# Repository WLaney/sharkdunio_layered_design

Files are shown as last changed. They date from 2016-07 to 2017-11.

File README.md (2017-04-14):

# sharkduino_layered_desgine

This repository contains the Eagle designs and design information for the Sharkduino PCBs. The name sharkduino_layered_desgin is a legacy name referring to the design type used by Sharkduino V1. This repository does however contains all versions of Shakrduino, not just V1. Please see [Sharkduino Versions](#sharkduino-versions) for more information. For the spefic chips and ports on each version please see [Hardware Quick Reference](https://github.com/WLaney/sharkdunio_layered_design/blob/master/hardware_quick_reference.md)

# Sharkduino Versions

This is an explanation of the different sharkduino versions and the directories in this repository that contain them

## Sharkduino V1

Sharkduino V1 uses a layer designs and consists of [layer1](layer1/), [layer2](layer2/), and [layer3](layer3/). The versions of Sharkduino V1 that were assembled corresponded to the release v2 named "Layered boards". Changes have been made to the boards since then in order to improve them, these changes constitute Sharkduino V1.1. No V1.1 boards were ever ordered or assembled. Instead of ordering V1.1 boards a design overhaul took place and we moved to Sharkduino V2. 

## Sharkduino V2

Sharkduino V2 constitutes a design overhaul from V1 with a new board shape and new set of sensors. These designs can be found in the [trapezoid](trapezoid/) directory. The version of Sharkduino V2 that has been assembled corresponds to release [v5](https://github.com/WLaney/sharkdunio_layered_design/releases/tag/v5) "Sharkduion V2". Since the enviromental sensors need to be sepreate from the movement sensors Shakrduino V2 still uses [layer3](layer3/) form the Sharkduino V1 as no changes to that board were nessary.

## Sharkduino V2.1

Sharkduino V2.1 is an identical PCB to V2, but it uses the MMA8451 accelerometer. This is opposed to the MMA8452 used in the V2. This change was made so that the accelerometer would have a FIFO bufer like the gyroscope. The new accelerometer is an expermental change, so the files are on the [MMA8451 branch](https://github.com/WLaney/sharkdunio_layered_design/tree/mma8451). The first functinoal build of this corosponds to release [v7](https://github.com/WLaney/sharkdunio_layered_design/releases/tag/v7). The change on this branch have since been merged into master.

## Sharkduino V2.2

Sharkduino V2.2 is a slight varation on the Sharkduino V2.x desgine. Due to the [issue with the cargining circuity](https://github.com/WLaney/sharkdunio_layered_design/issues/1) the microUSB and lipo charger were removed from the board. This was done in order to have a set of fully functional board ready for summer 2017. 

The LiPo plug was moved to the top of the board in order to streamline the desgine. Additionaly interupt pin2 on the FXAS21002 gyroscope was connected Arduino pin 2. 

Since in the long term we plan to fix the LiPo charging issue, instead of removing the LiPo chargin all together as we have done here, the files for Sharkduino V2.2 are on the [no_chargin branch](https://github.com/WLaney/sharkdunio_layered_design/tree/no_charging) and will never be merged into master. The desgines of the Sharkduino V2.2 that have been order corosponed to release [v8](https://github.com/WLaney/sharkdunio_layered_design/releases/tag/v8).

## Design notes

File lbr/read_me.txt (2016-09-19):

The abracon lbr comes form the following source:
https://github.com/cmonr/Eagle-Libraries/blob/master/Other/abracon.lbr
I have checked it for the abs25 and it looks good. I increased the size of the silk scrren wire width, and added a tdoc layer. The silk sreen crosses the pads, instead of fixing it I'll let the fab house just not print it

the sharkduino lbr is created in full by me

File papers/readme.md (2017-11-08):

# Papers

This directroy contains datasheets for componets on the tag that do not inteact with the Arduino through code. For the reamind data sheets please look in the [Arduino_Animal_Tag repo](https://github.com/sharkduino/Arduino_Animal_Tag/tree/master/papers)

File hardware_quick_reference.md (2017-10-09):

## Sharkduino V1.0
* MMA8452Q Accelerometer
* L3GD20H Gyroscope
* DS3234 RTC
  * Interrupt wired to Arduino pin 2
* Push-Push microSD slot
* JPL male 2 prong connector
* [Broken] MCP7381 LiPo Charge Management Controller
* [Broken] Micro USB female port
* 12mm coin cell slot
### On separate layer 3 board
* TMP102 Temperature Sensor
* MS5803 Temp/Pressure Sensor

## Sharkduino V2.0
*Full Redesign*
* MMA8452Q Accelerometer
  * INT1 pin wired to Arduino pin 3
* FXAS21002 Gyroscope
* DS1339B RTC
  * Interrupt wired to Arduino pin 2
* Push-Pull microSD slot
* JPL male 2 prong connector
* [Broken] MCP7381 LiPo Charge Management Controller
* [Broken] Micro USB female port
* 12mm coin cell slot
### On separate layer 3 board
* TMP102 Temperature Sensor
* MS5803 Temp/Pressure Sensor

## Sharkduino V2.1
*New accelerometer: MMA8451Q*
* MMA8451Q Accelerometer
  * INT1 pin wired to Arduino pin 3
* FXAS21002 Gyroscope
* DS1339B RTC
  * Interrupt wired to Arduino pin 2
* Push-Pull microSD slot
* JPL male 2 prong connector
* [Broken] MCP7381 LiPo Charge Management Controller
* [Broken] Micro USB female port
* 12mm coin cell slot
### On separate layer 3 board
* TMP102 Temperature Sensor
* MS5803 Temp/Pressure Sensor

## Sharkduino V2.2
*Connected FXAS21002 Gyroscope interupt*

*Removed MCP7381 LiPo Charge Management Controller*

*Removed Micro USB female port*
* MMA8451Q Accelerometer
  * INT1 pin wired to Arduino pin 3
* FXAS21002 Gyroscope
  * INT2 pin wired to Arduino pin 2
* DS1339B RTC
  * Interrupt wired to Arduino pin 2
* Push-Pull microSD slot
* JPL male 2 prong connector
* 12mm coin cell slot
### On separate layer 3 board
* TMP102 Temperature Sensor
* MS5803 Temp/Pressure Sensor

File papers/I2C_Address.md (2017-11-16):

# I2C Address

Found using I2C scaner on V2.2B and V2.0A

| device    | i2c address |
| --------- | ----------- |
| DS1339B   | 0x68        |
| FXAS21002 | 0x20        |
| MMA8451   | 0x1D        |

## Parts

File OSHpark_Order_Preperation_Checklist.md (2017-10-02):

# OSHpark Order Preparation Checklist

* Run Ratsnest and confirm no air wires
* Confirm that all desired pours are accounted for
* Estimate grounding paths on the board and determine if extra ground lines or vias are needed
* Check for non optimal traces on board
* Check for right angle traces on data lines
* Run [oshpark-2layer DRC](http://docs.oshpark.com/design-tools/eagle/design-rules-files/)
* Run [SparkFun DRC](https://www.sparkfun.com/tutorials/115)
  * Please note that this DRC will throw errors for tolerance that OSHpark can handle, when in doubt trust the OSH Park DRC
* Run [oshpark-2layer DRC](http://docs.oshpark.com/design-tools/eagle/design-rules-files/) again
* Run ERC
* If multiple trace sizes are used confirm that they are consistent, and that traces have the same width for there full length
* check components on board against the BOM
* Confirm that all components are labeled on silk
* Confirm that all pins are labeled on silk
* If orientation is important confirm that it is correct and clearly labeled on silk
* Confirm that all product and author info is on silk
* Confirm that all writing on silk is correctly spelled
* Confirm that no silk overlaps exposed copper
* Smash all components
* Delete all tNames and bNames (layers 25 and 26 respectively)
* Upload designs to OSHpark
* Confirm that silk looks good, and writing is positioned correctly
* Confirm that traces look as desired

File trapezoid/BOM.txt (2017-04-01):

component/value, size, quanity, digikey part number
--------------------------------------------------------
Arduino Pro Mini 3.3V/8MHz, NA, 1, 1568-1054-ND
MMA8451QT, 16-VFQFN, 1, MMA8451QT-ND
FXAS21002 IC, 24-TFQFN, 1, FXAS21002CQR1CT-ND
DS1339B IC, 8-TSSOP/8-MSOP, 1, DS1339BU+-ND
Abracon LLC ABS25-32.768KHZ-T, 4-SOJ, 1, 535-9166-1-ND
MCP73831 IC, SC-74A/SOT-753, 1, MCP73831T-2ATI/OTCT-ND
Molex 8+2 microSD slot, NA, 1, WM6357CT-ND
Red LED, 0603, 1, 160-1447-1-ND
0.1uF capacitor, 0805, 6, 478-3755-1-ND
1.0uF capacitor, 0805, 1, 311-1365-1-ND
4.7uF capacitor, 0805, 3, 490-3335-1-ND
330 resistor, 0805, 1, 311-330CRCT-ND
2k resistor, 0805, 1, 311-2.00KCRCT-ND
10K resistor, 0805, 4, 311-10.0KCRCT-ND
47k resistor, 0805, 1, 311-47KARCT-ND
USB micro SMD, NA, 1, 609-4053-1-ND
Curved Battery Holder, 12mm, 1, 36-3000CT-ND
JST Male, 2mm, 1, 455-1749-1-ND
Male Header Pins, 0.10", 1, S1011EC-40-ND
BATTERY LITHIUM 3V COIN 12.5MM, BR1225, 1, P183-ND

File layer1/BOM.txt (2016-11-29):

component/value, size, quanity, digikey part number
--------------------------------------------------------
0.1uF capacitor, 0805, 4, 478-3755-1-ND
4.7uF capacitor, 0805, 1, 490-3335-1-ND
10uF capacitor, 0805, 1, 490-4735-1-ND
10K resistor, 0805, 4, 311-10.0KCRCT-ND
MMA8452QT, 16-VFQFN, 1, 	MMA8452QT-ND
L3GD20HTR IC, 16-LGA, 1, 497-13931-1-ND
microSD SMD, NA, 1, Sparkfun: PRT-00127

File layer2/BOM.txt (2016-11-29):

component/value, size, quanity, digikey part number
--------------------------------------------------------
4.7uF capacitor, 0805, 2, 490-3335-1-ND
22pF capacitor, 0402, 1, 399-7774-1-ND
Red LED, 0603, 1, 160-1447-1-ND
10K resistor, 0805, 1, 311-10.0KCRCT-ND
2k resistor, 0805, 1, 311-2.00KCRCT-ND
330 resistor, 0805, 1, 311-330CRCT-ND
DS3234 IC, 20-SOIC, 1, 	DS3234S#T&RCT-ND
MCP73831 IC, SC-74A/SOT-753, 1, MCP73831T-2ATI/OTCT-ND
Curved Battery Holder, 12mm, 1, 36-3000CT-ND
JST Male, 2mm, 1, 455-1749-1-ND
USB micro SMD, NA, 1, 609-4053-1-ND
Header Pins, NA, 1, S1131EC-40-ND

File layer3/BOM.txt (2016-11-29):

component/value, size, quanity, digikey part number
--------------------------------------------------------
10K resistor, 0805, 1, 311-10.0KCRCT-ND
2.2K resistor, 0805, 2, 311-2.20KCRCT-ND
1k resostor, 0805, 1, 311-1.00KCRCT-ND
0.1uF capacitor, 0805, 2, 478-3755-1-ND
TMP102 IC, SOT-563/SOT-666, 1, 296-26834-1-ND
MS5803-14BA IC, NA, 1, 223-1626-5-ND

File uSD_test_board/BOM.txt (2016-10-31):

component/value, size, quanity, digikey part number
--------------------------------------------------------
Molex 8+2 microSD slot, NA, 1, WM6357CT-ND
Amphenol 8+2 microSD slot, NA, 114-00841-68-1-ND
Hirose 8+2 microSD slot, NA, HR1941CT-ND

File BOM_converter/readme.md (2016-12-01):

# BOM Convertor

This is a simple python script that converts the BOM format used in the Sharkduino project into a format that can be directly uploaded into DigiKey's BOM Manager.

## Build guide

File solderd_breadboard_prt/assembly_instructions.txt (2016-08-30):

Soldered Breadboard Assembly Instructions
=====================

(please note that these steps represent what I beilive to be the optimal order of operations. They may not be. Addionaly not all boards were assembled in this way as I expermented with the order)

1) Cut perfreated breadboard to the correct size
2) Solder Headers onto the breadboard
3) Solder wires that run on the top of the board. Start with VCC and GND conections as these are the longest
4) Creat nessary solder briges on the bottom
5) Solder in wires on the bottom
6) Insure that all nessary points are connected
7) Add extra support headers for the uSD, accel, and gyro
8) Solder I2C wires to the arduino
9) Place batt into RTC
10) Solder arduino, uSD holder, and RTC onto the board
11) Solder I2C wire into bread board
12) Solder on accel and gyro

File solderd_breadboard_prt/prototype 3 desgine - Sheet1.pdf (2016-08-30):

V | G | S | SCL | G | | S | S | V | S | H | H | H | H | H | H | H | H | | | 9 | | | | | 2 | G
| | | | | | | | | | DI | | | | | | | | | CD
| | | | | SCL | | | | | D0 | | | | | | | | | D0
| | | | | SDA | | | | CK | | | | | | | | G
| | | | | | | | | | SW | | | ck | | | | | CK | | | | | | | | S | SCL
| | | | | | | | | | V | | | | | | | | | V
| | | | | | | | | | G | | | | | | | | | DI | | 10 | 11 | 12 | 13 | | | V | G | R
| | | | | | | | | | | | | | | | | | | CS

G V S C D DI

S | G | V | V S | G

SS

SCL

SDA

SDA | SCL

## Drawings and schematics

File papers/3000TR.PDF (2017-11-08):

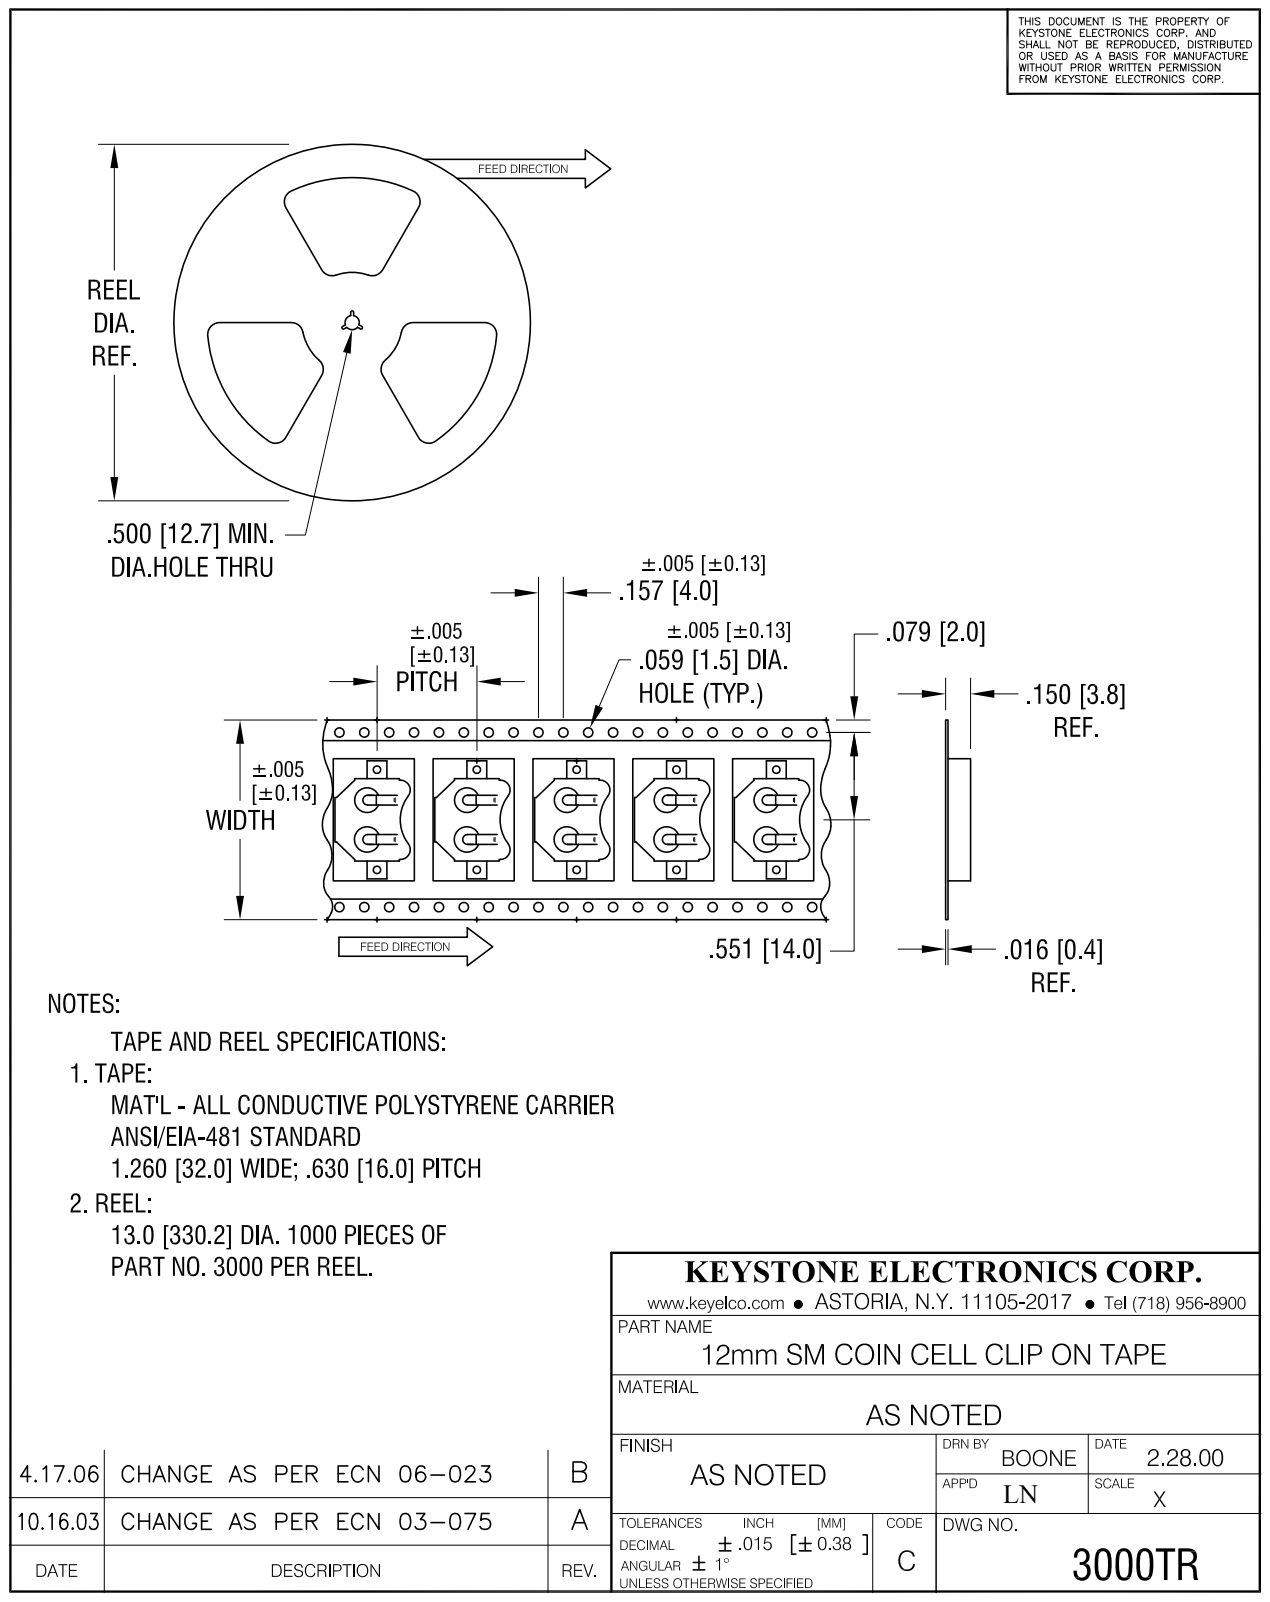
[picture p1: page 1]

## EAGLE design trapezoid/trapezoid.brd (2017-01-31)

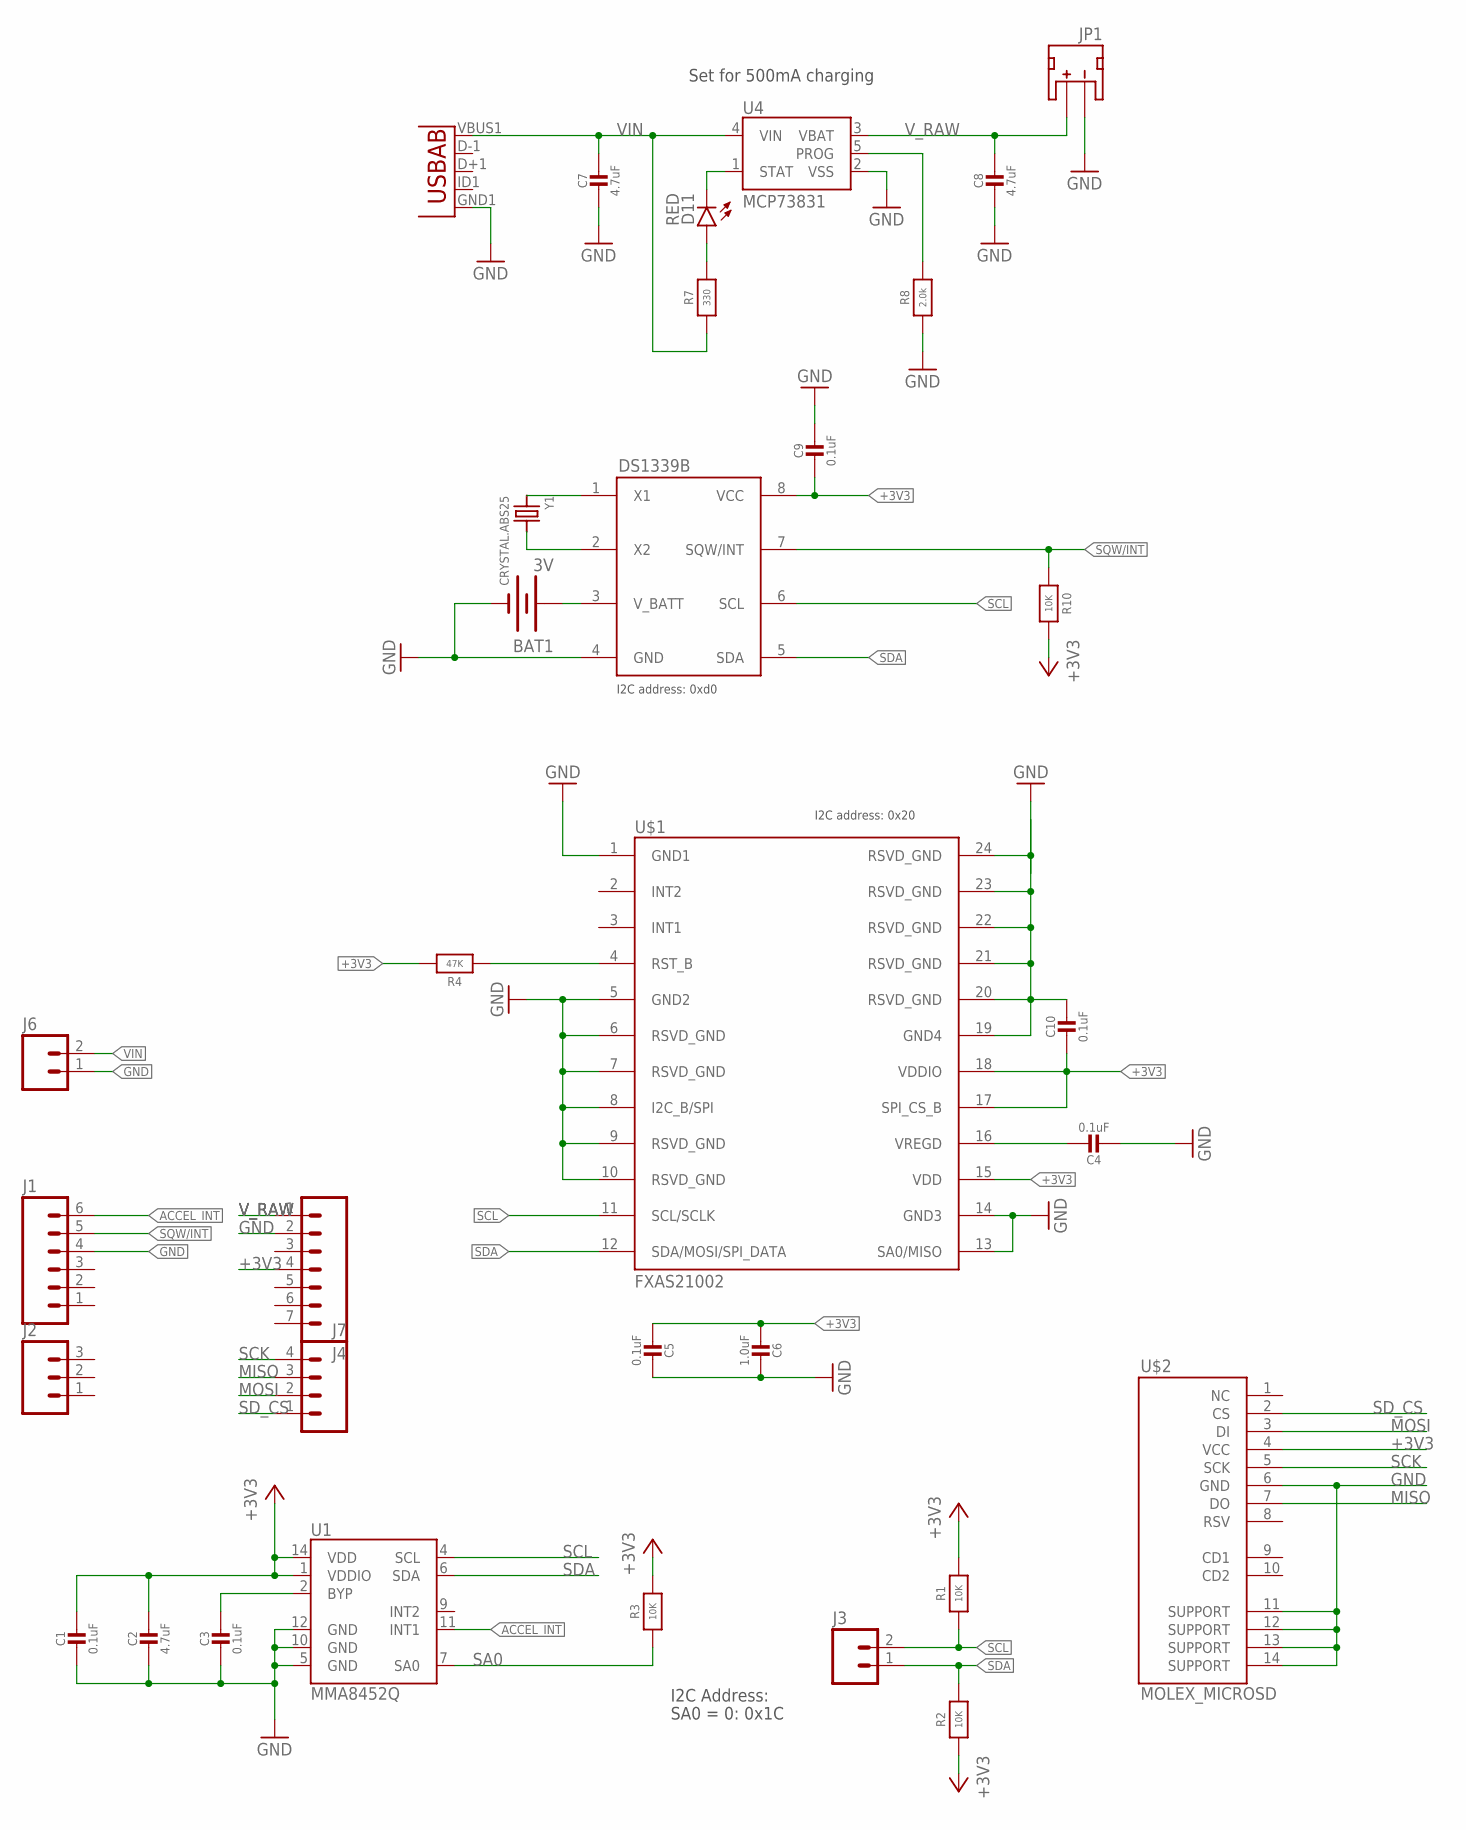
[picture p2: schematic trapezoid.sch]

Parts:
BAT1: 3V; BATTCON_12MM_CURVED
C1, C3, C4, C5, C9, C10: 0.1uF; 0805-NO
C2, C7, C8: 4.7uF; 0805-NO
C6: 1.0uF; 0805-NO
D11: RED; LED-0603
J1: M06SILK_FEMALE_PTH; 1X06
J2: M03PTH; 1X03
J3, J6: M02LOCK; 1X02_LOCK
J4: M07; 1X07
J7: M04PTH; 1X04
JP1: JST; JST-2-SMD@1
JP9: Micro USB; USB-AB-MICRO-SMD_V03
R1, R2, R10: 10K; 0805-NO
R3: 10K; _0805MP
R4: 47K; 0805-NO
R7: 330; _0805MP
R8: 2.0k; _0805MP
U1: MMA8452Q; QFN-16_0.5MM
U4: MCP73831; SOT23-5
U$1: FXAS21002; 24QFN
U$2: MOLEX_MICROSD
U$3: DS1339BDS1339B; 8U-SOP
Y1: CRYSTAL.ABS25; ABS25

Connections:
+3V3: C1.1, C2.1, C5.2, C6.2, C9.2, C10.2, J4.4, R1.2, R2.1, R3.2, R4.2, R10.2, U1.1 (VDDIO), U1.14 (VDD), U$1.15 (VDD), U$1.17 (SPI_CS_B), U$1.18 (VDDIO), U$2.4 (VCC), U$3.8 (VCC)
ACCEL_INT: J1.6, U1.11 (INT1)
BYP: C3.1, U1.2 (BYP)
GND: BAT1.GND (-), C1.2, C2.2, C3.2, C4.2, C5.1, C6.1, C7.2, C8.2, C9.1, C10.1, J1.4, J4.2, J6.1, JP1.1 (-), JP9.GND1 (GND), R8.1, U1.5 (GND), U1.10 (GND), U1.12 (GND), U4.2 (VSS), U$1.1 (GND1), U$1.5 (GND2), U$1.6 (RSVD_GND), U$1.7 (RSVD_GND), U$1.8 (I2C_B/SPI), U$1.9 (RSVD_GND), U$1.10 (RSVD_GND), U$1.13 (SA0/MISO), U$1.14 (GND3), U$1.19 (GND4), U$1.20 (RSVD_GND), U$1.21 (RSVD_GND), U$1.22 (RSVD_GND), U$1.23 (RSVD_GND), U$1.24 (RSVD_GND), U$2.6 (GND), U$2.11 (SUPPORT), U$2.12 (SUPPORT), U$2.13 (SUPPORT), U$2.14 (SUPPORT), U$3.4 (GND)
MISO: J7.3, U$2.7 (DO)
MOSI: J7.2, U$2.3 (DI)
unnamed: D11.A, R7.2
unnamed: U$3.2 (X2), Y1.4 (2)
unnamed: C4.1, U$1.16 (VREGD)
unnamed: BAT1.PWR@1 (+), U$3.3 (V_BATT)
unnamed: U$3.1 (X1), Y1.1
unnamed: R4.1, U$1.4 (RST_B)
PROG: R8.2, U4.5 (PROG)
SA0: R3.1, U1.7 (SA0)
SCK: J7.4, U$2.5 (SCK)
SCL: J3.2, R1.1, U1.4 (SCL), U$1.11 (SCL/SCLK), U$3.6 (SCL)
SDA: J3.1, R2.2, U1.6 (SDA), U$1.12 (SDA/MOSI/SPI_DATA), U$3.5 (SDA)
SD_CS: J7.1, U$2.2 (CS)
SQW/INT: J1.5, R10.1, U$3.7 (SQW/INT)
STAT: D11.C, U4.1 (STAT)
VIN: C7.1, J6.2, JP9.VBUS1 (VBUS), R7.1, U4.4 (VIN)
V_RAW: C8.1, J4.1, JP1.2 (+), U4.3 (VBAT)

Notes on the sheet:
I2C Address:
SA0 = 0: 0x1C
Set for 500mA charging
I2C address: 0xd0
I2C address: 0x20

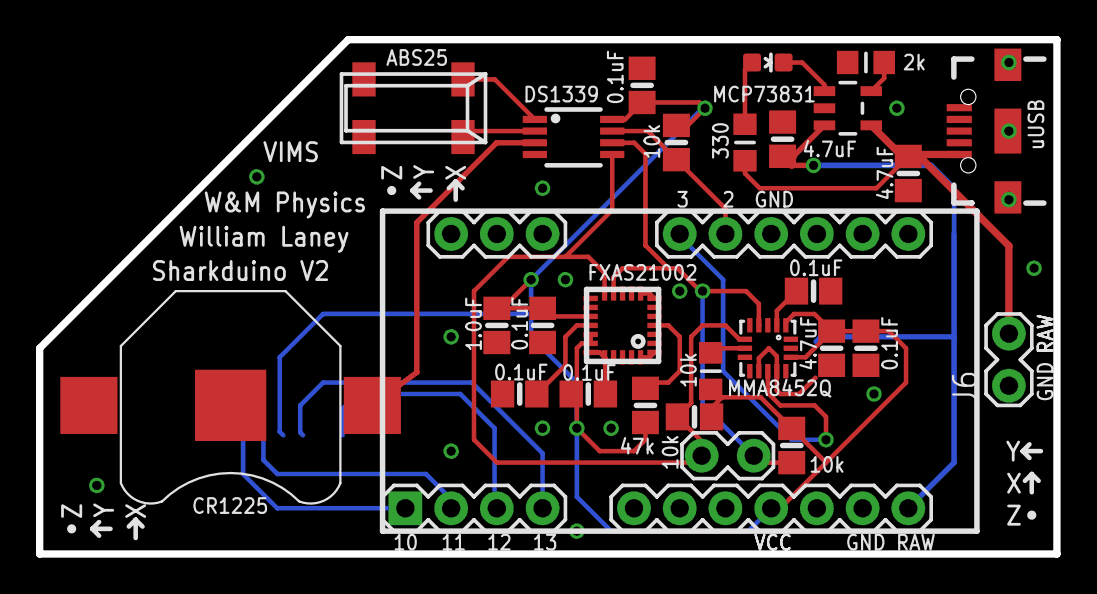
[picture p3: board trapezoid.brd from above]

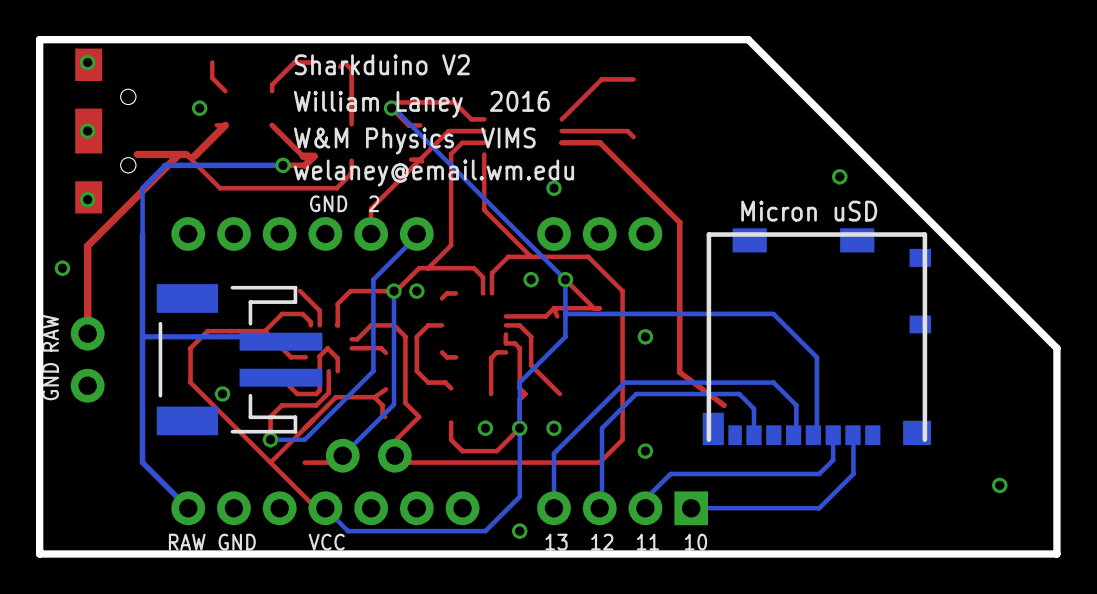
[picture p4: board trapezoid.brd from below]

Board: 2 copper layers, 56.5 x 28.6 mm, 33 parts (2 on the bottom side), 22 nets.

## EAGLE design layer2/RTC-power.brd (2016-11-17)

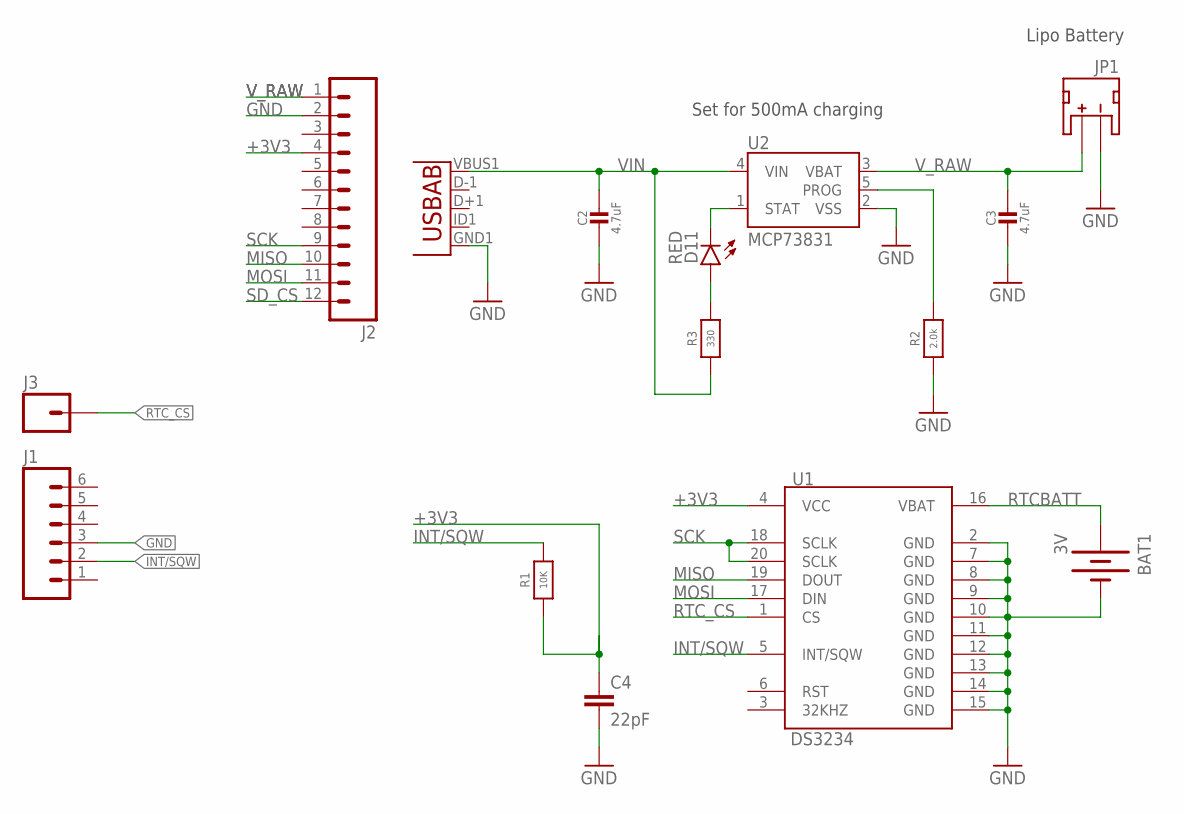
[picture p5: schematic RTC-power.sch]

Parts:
BAT1: 3V; BATTCON_12MM_CURVED
C2, C3: 4.7uF; 0805-NO
C4: 22pF; 0402-CAP
D11: RED; LED-0603
J1: M06SILK_FEMALE_PTH; 1X06
J2: M12PTH; 1X12
J3: M01PTH; 1X01
JP1: JST; JST-2-SMD@1
JP9: Micro USB; USB-AB-MICRO-SMD_V03
R1: 10K; _0805MP
R2: 2.0k; _0805MP
R3: 330; _0805MP
U1: DS3234
U2: MCP73831; SOT23-5

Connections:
+3V3: C4.1, J2.4, R1.1, U1.4 (VCC)
GND: BAT1.GND (-), C2.2, C3.2, C4.2, J2.2, JP1.1 (-), JP9.GND1 (GND), R2.1, U1.2 (GND), U1.7 (GND), U1.8 (GND), U1.9 (GND), U1.10 (GND), U1.11 (GND), U1.12 (GND), U1.13 (GND), U1.14 (GND), U1.15 (GND), U2.2 (VSS)
INT/SQW: R1.2, U1.5 (INT/SQW)
MISO: J2.10, U1.19 (DOUT)
MOSI: J2.11, U1.17 (DIN)
unnamed: D11.A, R3.2
PROG: R2.2, U2.5 (PROG)
RTCBATT: BAT1.PWR@1 (+), U1.16 (VBAT)
RTC_CS: J3.1, U1.1 (CS)
SCK: J2.9, U1.18 (SCLK), U1.20 (SCLK)
SD_CS: J2.12
STAT: D11.C, U2.1 (STAT)
VIN: C2.1, JP9.VBUS1 (VBUS), R3.1, U2.4 (VIN)
V_RAW: C3.1, J2.1, JP1.2 (+), U2.3 (VBAT)

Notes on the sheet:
Set for 500mA charging
Lipo Battery

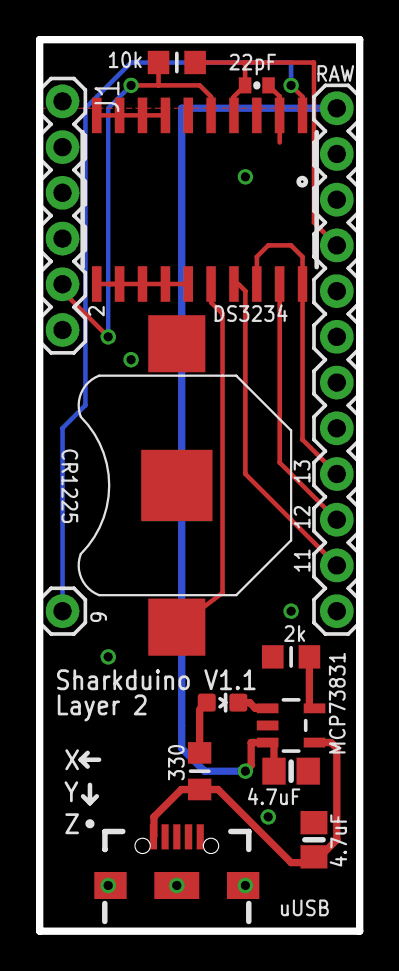
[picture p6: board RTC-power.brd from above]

Board: 2 copper layers, 17.8 x 49.5 mm, 15 parts (1 on the bottom side), 13 nets.

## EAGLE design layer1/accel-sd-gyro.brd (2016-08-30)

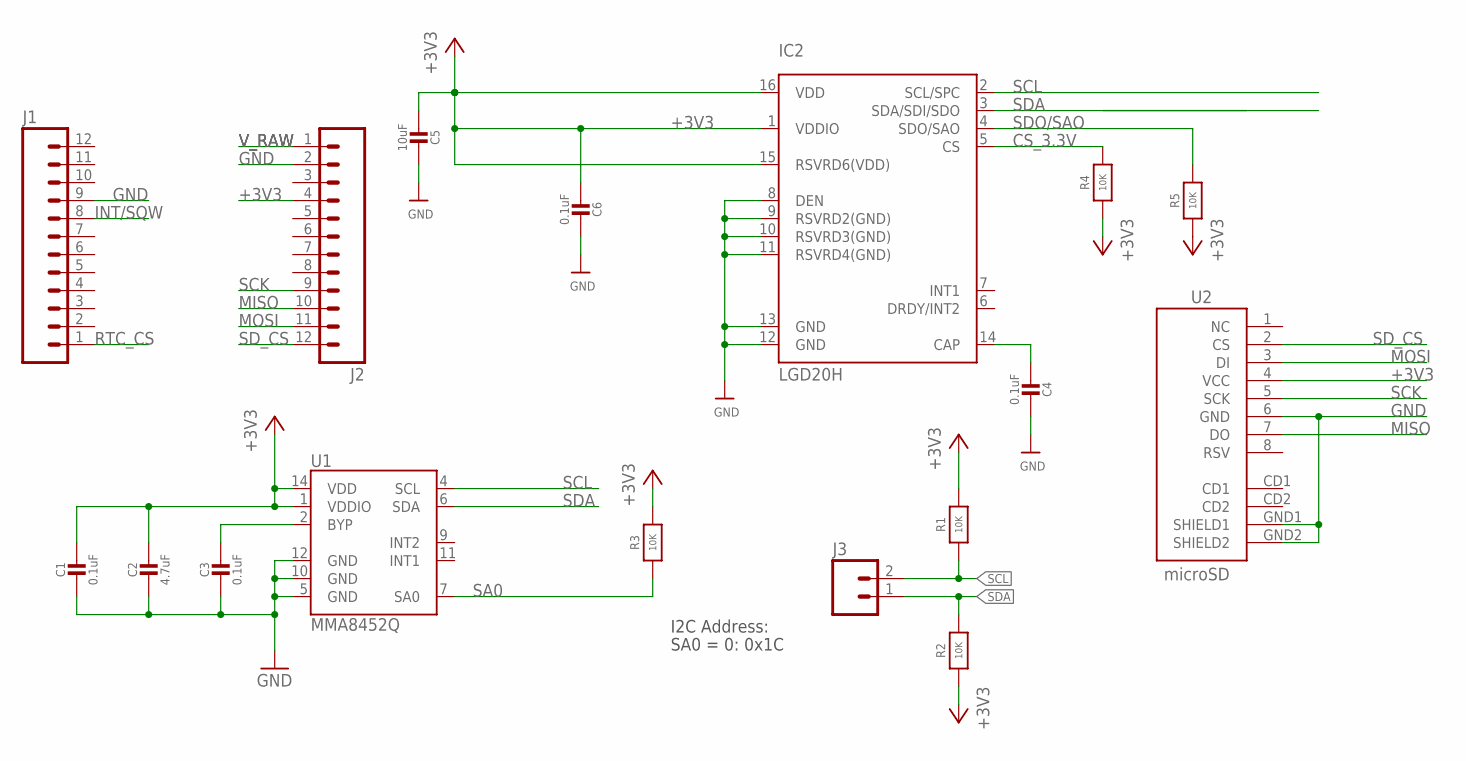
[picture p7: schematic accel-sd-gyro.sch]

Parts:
C1, C3, C4, C6: 0.1uF; 0805-NO
C2: 4.7uF; 0805-NO
C5: 10uF; 0805-NO
IC2: LGD20H; L3GD20H_LGA16L
J1, J2: M12PTH; 1X12
J3: M02LOCK; 1X02_LOCK
R1, R2, R4, R5: 10K; 0805-NO
R3: 10K; _0805MP
U1: MMA8452Q; QFN-16_0.5MM
U2: microSD; MICRO-SD-SOCKET-PP

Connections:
+3V3: C1.1, C2.1, C5.2, C6.2, IC2.1 (VDDIO), IC2.15 (RSVRD6(VDD)), IC2.16 (VDD), J2.4, R1.2, R2.1, R3.2, R4.1, R5.1, U1.1 (VDDIO), U1.14 (VDD), U2.4 (VCC)
BYP: C3.1, U1.2 (BYP)
CS_3.3V: IC2.5 (CS), R4.2
GND: C1.2, C2.2, C3.2, C4.1, C5.1, C6.1, IC2.8 (DEN), IC2.9 (RSVRD2(GND)), IC2.10 (RSVRD3(GND)), IC2.11 (RSVRD4(GND)), IC2.12 (GND), IC2.13 (GND), J1.9, J2.2, U1.5 (GND), U1.10 (GND), U1.12 (GND), U2.6 (GND), U2.GND1 (SHIELD1), U2.GND2 (SHIELD2)
INT/SQW: J1.8
MISO: J2.10, U2.7 (DO)
MOSI: J2.11, U2.3 (DI)
unnamed: C4.2, IC2.14 (CAP)
RTC_CS: J1.1
SA0: R3.1, U1.7 (SA0)
SCK: J2.9, U2.5 (SCK)
SCL: IC2.2 (SCL/SPC), J3.2, R1.1, U1.4 (SCL)
SDA: IC2.3 (SDA/SDI/SDO), J3.1, R2.2, U1.6 (SDA)
SDO/SAO: IC2.4 (SDO/SAO), R5.2
SD_CS: J2.12, U2.2 (CS)
V_RAW: J2.1

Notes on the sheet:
I2C Address:
SA0 = 0: 0x1C

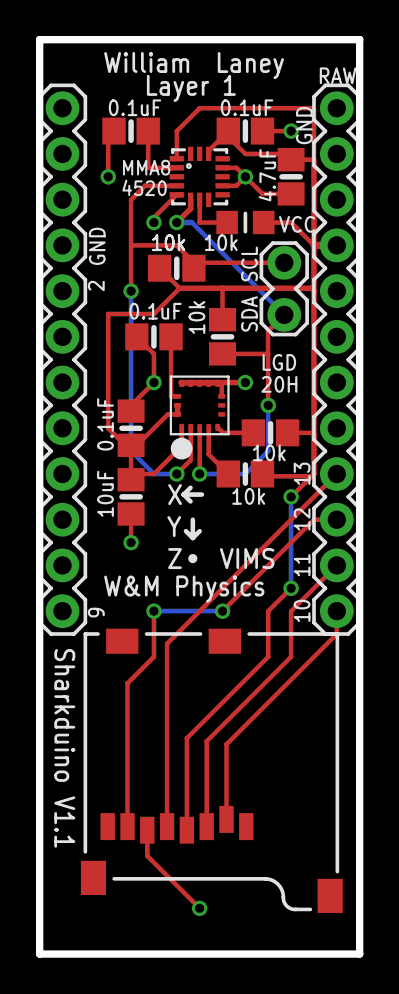
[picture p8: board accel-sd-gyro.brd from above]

Board: 2 copper layers, 17.8 x 50.8 mm, 17 parts (0 on the bottom side), 13 nets.

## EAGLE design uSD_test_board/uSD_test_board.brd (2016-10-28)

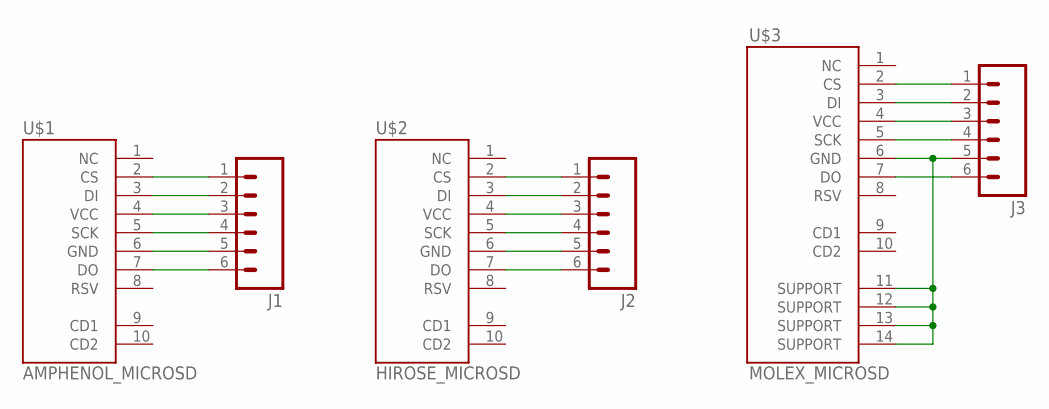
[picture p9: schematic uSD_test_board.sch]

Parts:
J1, J2, J3: M06SILK_FEMALE_PTH; 1X06
U$1: AMPHENOL_MICROSD
U$2: HIROSE_MICROSD; AMPHENOL_MICROSD
U$3: MOLEX_MICROSD

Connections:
CS1: J1.1, U$1.2 (CS)
CS2: J2.1, U$2.2 (CS)
CS3: J3.1, U$3.2 (CS)
DI1: J1.2, U$1.3 (DI)
DI2: J2.2, U$2.3 (DI)
DI3: J3.2, U$3.3 (DI)
DO1: J1.6, U$1.7 (DO)
DO2: J2.6, U$2.7 (DO)
DO3: J3.6, U$3.7 (DO)
GND: J1.5, J2.5, J3.5, U$1.6 (GND), U$2.6 (GND), U$3.6 (GND), U$3.11 (SUPPORT), U$3.12 (SUPPORT), U$3.13 (SUPPORT), U$3.14 (SUPPORT)
SCK1: J1.4, U$1.5 (SCK)
SCK2: J2.4, U$2.5 (SCK)
SCK3: J3.4, U$3.5 (SCK)
VCC1: J1.3, U$1.4 (VCC)
VCC2: J2.3, U$2.4 (VCC)
VCC3: J3.3, U$3.4 (VCC)

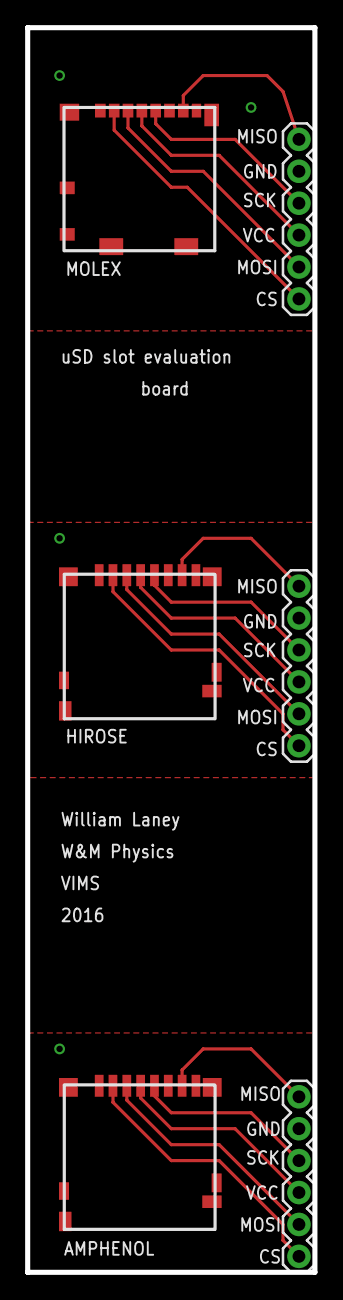
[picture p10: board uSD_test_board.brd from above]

Board: 2 copper layers, 22.9 x 99.1 mm, 6 parts (0 on the bottom side), 16 nets.

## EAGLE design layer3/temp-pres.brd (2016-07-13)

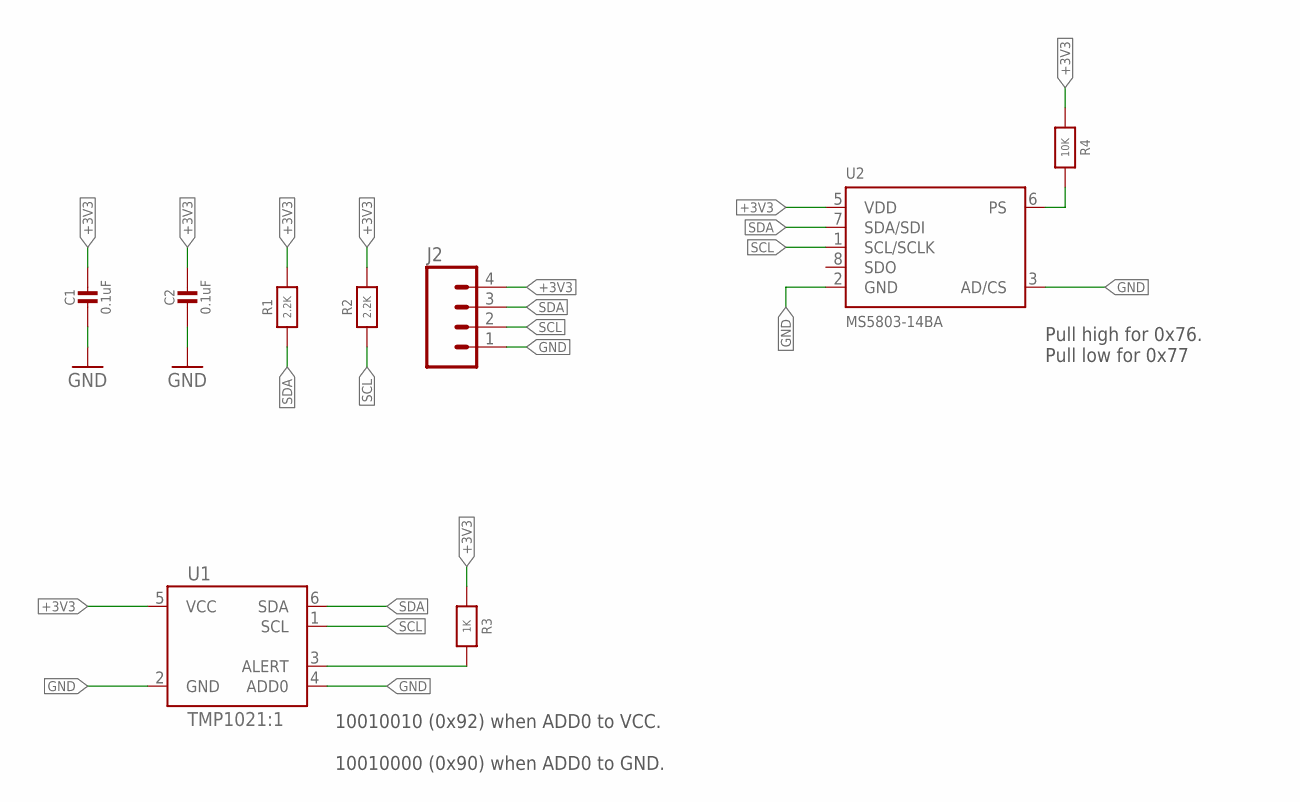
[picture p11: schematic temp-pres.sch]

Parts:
C1, C2: 0.1uF; 0805-NO
J2: M04NO_SILK_ALL_ROUND; 1X04_NO_SILK_ALL_ROUND
R1, R2: 2.2K; _0805MP
R3: 1K; _0805MP
R4: 10K; _0805MP
U1: TMP1021:1; SOT563-2
U2: MS5803-14BA; MS5803

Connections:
+3V3: C1.1, C2.1, J2.4, R1.2, R2.2, R3.1, R4.1, U1.5 (VCC), U2.5 (VDD)
GND: C1.2, C2.2, J2.1, U1.2 (GND), U1.4 (ADD0), U2.2 (GND), U2.3 (AD/CS)
unnamed: R3.2, U1.3 (ALERT)
PS: R4.2, U2.6 (PS)
SCL: J2.2, R2.1, U1.1 (SCL), U2.1 (SCL/SCLK)
SDA: J2.3, R1.1, U1.6 (SDA), U2.7 (SDA/SDI)

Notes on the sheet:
10010010 (0x92) when ADD0 to VCC. 10010000 (0x90) when ADD0 to GND.
Pull high for 0x76. Pull low for 0x77

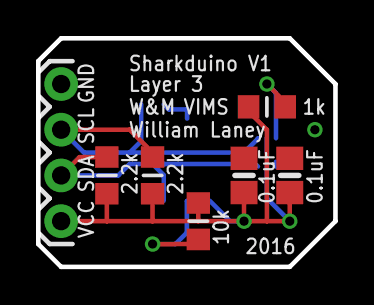
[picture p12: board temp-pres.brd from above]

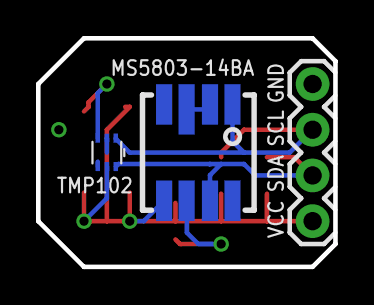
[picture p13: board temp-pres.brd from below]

Board: 2 copper layers, 16.5 x 12.7 mm, 9 parts (2 on the bottom side), 6 nets.

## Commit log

2016-06-10 creaded design file
    [layer1v1.brd, layer1v1.sch]
2016-06-10 added batteri connection to board
    [layer1v1.brd, layer1v1.sch]
2016-06-10 I don't know why eagles file thing hates me, but here we are
    [layer1v2.brd, layer1v2.sch]
2016-06-10 removed battery, add accel
    [layer1v2.brd]
2016-06-13 who needs commits
    [layer1v2.brd]
2016-06-14 layer 1 with diff componets
    [accel-sd-gyro.sch]
2016-06-14 added gyro
    [accel-sd-gyro.sch]
2016-06-14 added sd
    [accel-sd-gyro.sch]
2016-06-14 added headers
    [accel-sd-gyro.sch]
2016-06-14 finishing touches on schematic
    [accel-sd-gyro.sch]
2016-06-14 creaded layout
    [accel-sd-gyro.brd]
2016-06-15 created layout for just the gyro
    [accel-sd-gyro.brd, gyro.brd, gyro.sch]
2016-06-15 boards rounted with silk screen
    [gyro.brd, gyro.sch]
2016-06-15 shortedn connections, removed via
    [gyro.brd, gyro.sch]
2016-06-15 rottated header 180 degrees
    [gyro.brd]
2016-06-15 added six pin header to stack with accell
    [gyro.brd, gyro.sch]
2016-06-15 set up pins to line up with accel corectly
    [gyro.brd, gyro.sch]
2016-06-15 minor placment adjustments
    [gyro.brd]
2016-06-16 final touches
    [gyro.brd]
2016-06-16 final verson to submit to osh park for protyping
    [gyro.brd]
2016-06-16 adjusted tname and tvalue layers
    [gyro.brd]
2016-06-17 adjusted silk screen layout
    [gyro.brd]
2016-06-23 intial layout of v2 board, consldated i2c resisor, added header pin row
    [accel-sd-gyro.brd, accel-sd-gyro.sch]
2016-06-24 layer 1 tweaks and silk
    [accel-sd-gyro.brd, accel-sd-gyro.sch]
2016-06-27 begun layer 2 desgine
    [RTC-power.sch, accel-sd-gyro.brd]
2016-06-27 Initail board argment
    [RTC-power.sch]
2016-06-27 real intial board layout
    [RTC-power.brd]
2016-06-28 layed out all conectons on board
    [RTC-power.brd, RTC-power.sch]
2016-06-28 replaced ground wires with top layer ground plane
    [RTC-power.brd]
2016-06-28 removed unneeded header to give battery access
    [RTC-power.brd, RTC-power.sch]
2016-06-28 silk screen adjustment
    [RTC-power.brd, RTC-power.sch, accel-sd-gyro.brd]
2016-06-28 silk screen
    [RTC-power.brd, accel-sd-gyro.brd, accel-sd-gyro.sch]
2016-06-30 increased charging wire width
    [RTC-power.brd]
2016-06-30 added bottom silk screen
    [RTC-power.brd, accel-sd-gyro.brd]
2016-07-05 removed via under sd
    [RTC-power.brd, accel-sd-gyro.brd]
2016-07-05 tweaked silk screen and spread out some componets slightly
    [RTC-power.brd, accel-sd-gyro.brd]
2016-07-06 added bill of materials
2016-07-06 slight tweaks
    [accel-sd-gyro.brd]
2016-07-07 tweacked sd traces
    [accel-sd-gyro.brd, accel-sd-gyro.sch]
2016-07-07 final chnages before ordering
    [RTC-power.brd, accel-sd-gyro.brd]
2016-07-08 created pressure sensor temp sensor sychmatic
    [temp-pres.brd, temp-pres.sch]
2016-07-08 intital board layout
    [temp-pres.brd, temp-pres.sch]
2016-07-08 who knows, probably just opened the file
    [gyro.brd]
2016-07-08 diangonalized coners to make smaller
    [temp-pres.brd]
2016-07-08 removed serial data output (SDO) from schematic bc it is not needed. Since it is an output I blieve it is safe to let it float.
    [temp-pres.brd, temp-pres.sch]
2016-07-08 added silk screen
    [temp-pres.brd]
2016-07-11 added documentation of board
2016-07-11 removed residual layer1 directory
    [layer1v1.brd, layer1v1.sch, layer1v2.brd, layer1v2.sch]
2016-07-11 tweeaked resistor placement
    [temp-pres.brd]
2016-07-12 added clearnece between components and leads
    [temp-pres.brd]
2016-07-12 calrified commints
    [temp-pres.sch]
2016-07-13 tweaked layer3 silk screen for printing
    [temp-pres.brd, temp-pres.sch]
2016-08-05 slight tweaks to genrate images for poster
    [accel-sd-gyro.brd, accel-sd-gyro.sch]
2016-08-30 extned layer 1 length to fit uSD
    [accel-sd-gyro.brd]
2016-08-30 silk screen changes, added top ground pour, updated doc
    [accel-sd-gyro.brd]
2016-08-30 silk screen update
    [accel-sd-gyro.brd]
2016-08-30 removed pin 4, movved batt holder
    [RTC-power.brd, RTC-power.sch]
2016-08-30 add info about soldered protype
    add schematics and assembly instructions
2016-09-05 added prototype documentation
2016-09-16 created trapazoid layout
    [trapezoid.brd, trapezoid.sch]
2016-09-16 postiotedn arduino pins on board
    [trapezoid.brd]
2016-09-16 postiotend arduino pins on board correctly
    [trapezoid.brd]
2016-09-16 possistioned i2c pins
    [trapezoid.brd]
2016-09-17 clean up
    [trapezoid.brd]
2016-09-19 created ds1339b breakout schematic
    [DS1339B_RTC_breakout.sch]
2016-09-19 added information
    [DS1339B_RTC_breakout.sch]
2016-09-19 intial layout of breakout board
    [DS1339B_RTC_breakout.sch]
2016-09-20 created intial board layout
    [DS1339B_RTC_breakout.brd]
2016-09-20 updated documentation to reflect chargin circuit debugging
2016-09-26 final changes
    [DS1339B_RTC_breakout.brd]
2016-09-26 chnaged rtc to ds1339b in trap
    [trapezoid.brd, trapezoid.sch]
2016-09-26 rotated pro mini
    [trapezoid.brd]
2016-09-26 placed rtc and usd
    [trapezoid.brd, trapezoid.sch]
2016-09-26 placed accel and gyro
    [trapezoid.brd]
2016-09-27 fully connected schematics
    had to remove some header pin spots to run wire
    [trapezoid.brd, trapezoid.sch]
2016-09-27 decreased board size
    [trapezoid.brd]
2016-09-27 added gnd vias
    [trapezoid.brd]
2016-09-27 shifted everything so pro mini would not over hang board
    [trapezoid.brd]
2016-09-27 moved usb out form under pro mini
    [trapezoid.brd]
2016-09-29 put onto 0.025in grid
    [trapezoid.brd]
2016-09-29 corectly possitoned i2c pins
    [trapezoid.brd]
2016-09-30 compled intial layout and connections
    [trapezoid.brd]
2016-09-30 small optimizations
    [trapezoid.brd]
2016-10-13 centered arduino on board
    [trapezoid.brd]
2016-10-13 put uSD on bottom layer
    [trapezoid.brd]
2016-10-13 shortened board
    [trapezoid.brd]
2016-10-13 changed from 4pin to 3pin header to fit uSD
    [trapezoid.brd, trapezoid.sch]
2016-10-13 roated uUSB and shortened board
    [trapezoid.brd]
2016-10-13 fully routed
    [trapezoid.brd]
2016-10-16 small tweak
    [trapezoid.brd]
2016-10-16 updated doc to include ds1339 assembly instructions
2016-10-20 intial fxas gyro breakout schematic
    [FXAS21002_gyro.sch]
2016-10-20 chnaged i2c pull up resisotr to 10k
    this may not work, if that is the case its okay, I can just put a 4k7 resitor
    on the board,
    [FXAS21002_gyro.sch]
2016-10-20 created new gyro board
    [FXAS21002_gyro.brd]
2016-10-21 all wires connected
    [FXAS21002_gyro.brd]
2016-10-21 changed int2 pin
    did this to shorten trace to int2
    [FXAS21002_gyro.brd, FXAS21002_gyro.sch]
2016-10-21 added silk
    [FXAS21002_gyro.brd]
2016-10-21 added silk pin 1 dot
2016-10-21 pretty uped silk
    [FXAS21002_gyro.brd]
2016-10-21 unified units
    [FXAS21002_gyro.brd, FXAS21002_gyro.sch]
2016-10-24 created amphenol layout and device
2016-10-25 created molex uSD device
2016-10-27 cread schematic for uSD test board
    board will let me test three final uSD slots in consideration for sharkduino
    [uSD_test_board.sch]
2016-10-27 named nets
    [uSD_test_board.sch]
2016-10-27 created uSD test board
    [uSD_test_board.brd]
2016-10-28 prep for fab
    [FXAS21002_gyro.brd, uSD_test_board.brd]
2016-11-01 renamed layer1 directory
    [accel-sd-gyro.brd, accel-sd-gyro.sch]
2016-11-12 changed gyro in schematic
    [trapezoid.brd, trapezoid.sch]
2016-11-14 fully routed board
    [trapezoid.brd, trapezoid.sch]
2016-11-14 shortend routes
    [trapezoid.brd]
2016-11-14 add raw voltage headers
    allow for easy attachment of inductive charging
    [trapezoid.brd, trapezoid.sch]
2016-11-14 put new uSD slot on board
    [trapezoid.brd, trapezoid.sch]
2016-11-17 shrunk board
    [trapezoid.brd]
2016-11-17 moved uSD
    [trapezoid.brd]
2016-11-17 grounded uUSB
    [trapezoid.brd]
2016-11-18 preped for buying
    [trapezoid.brd]
2016-11-18 broke out accel int
    [trapezoid.brd, trapezoid.sch]
2016-11-18 final changes before order
    [trapezoid.brd]
2016-11-29 updaed layer 2 BOM JST conector
    changed the JST connector the correct one used in the schematics
2016-12-01 creaded procedues for OSH park order
    added checklist to insure board quality before it sent to be manufactured
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2017-01-23 unified trace width
    [trapezoid.brd]
2017-01-24 fixed external power headers
    conected external power headers to unrgulated side of rulgulator
    instead of regulated
    [trapezoid.brd, trapezoid.sch]
2017-01-24 solk screen tweak
    [trapezoid.brd]
2017-01-26 moved DS1339B, FXAS gyro, and L3 gyro to opensoure repos
    these repos can be found at:
    https://github.com/WLaney/DS1339B-RTC-PCB
    https://github.com/WLaney/FXAS21002-gyro-PCB
    https://github.com/WLaney/L3GD20H-gyro-PCB
    [DS1339B_RTC_breakout.brd, DS1339B_RTC_breakout.sch, FXAS21002_gyro.brd, FXAS21002_gyro.sch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]
2017-01-31 trap: small tweak to silk
    [trapezoid.brd]
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

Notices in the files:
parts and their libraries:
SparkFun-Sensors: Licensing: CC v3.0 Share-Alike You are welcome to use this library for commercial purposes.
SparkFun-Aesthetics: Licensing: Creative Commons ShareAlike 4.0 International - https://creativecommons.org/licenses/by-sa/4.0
